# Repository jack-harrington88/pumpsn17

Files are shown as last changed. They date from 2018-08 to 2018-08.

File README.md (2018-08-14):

# Perpetual Sedimentation (PS) Prototype

**This page describes how to build a perpetual sedimentation prototype housing three syringe pumps. These pumps allow for a continuous delivery of particles.**

This project is a fork of the original DropletKitchen project; [Low-cost, High-performance Syringe Pumps for Microfluidics Applications](https://github.com/DropletKitchen/pumpsn17). Original source code of the project is provided under MIT License. The source may contain code under a different license, if this is the case it is stated in the LICENSE file. 

The designs and documentation in this repository is Copyright (c) 2018 Jack Harrington and made available under a [Creative Commons Attribution 4.0 International (CC BY 4.0)](https://creativecommons.org/licenses/by/4.0/) License.

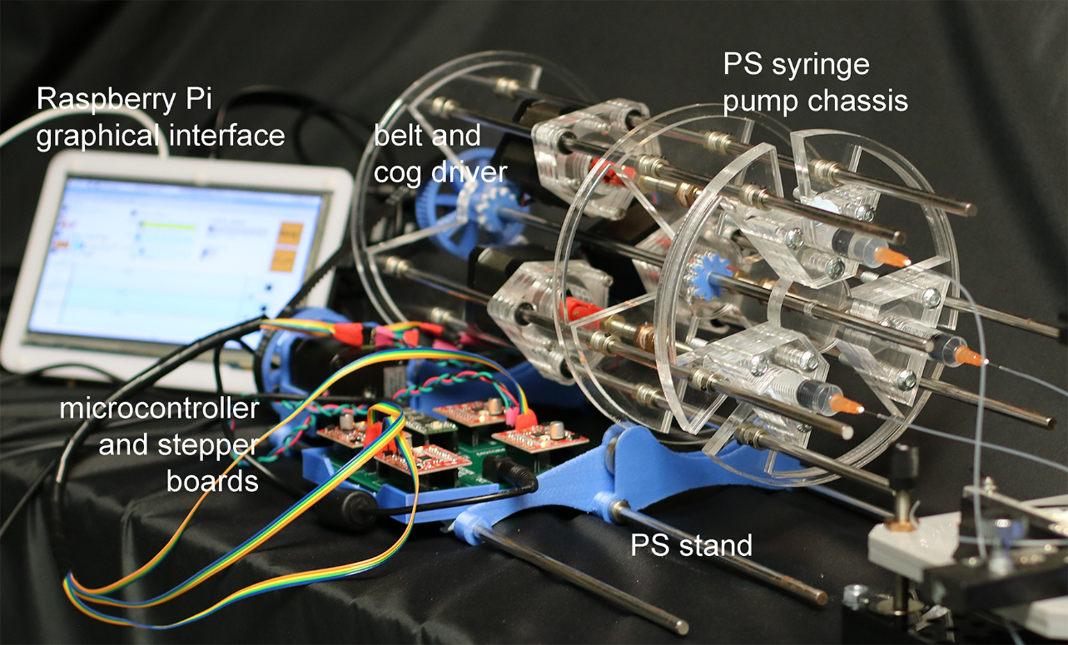
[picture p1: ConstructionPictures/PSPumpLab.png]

> The PS Pump prototype

## Introduction

The low-cost, high-performance syringe pumps from the droplet kitchen are suitable for a wide range of microfluidic applications, rivalling commercial pumps in quality at a fraction of the cost. The rapid sedimentation of particles often used in experiments (e.g. the DNA barcoded microbeads used in Drop-Seq) requires the use of expensive magnetic stirrers to actuate magnetic bars within the syringe. However, the DropSeq beads are fabricated using Toyopearl HW-65S resin, a brittle material that is prone to fracture during magnetic stirring. The perpetual sedimentation prototype provides a contactless solution to maintain particles in a suspended state to ensure continuous delivery.

The three PS syringe pumps work the same way as the original droplet kitchen pumps. The leadscrew is driven through a nut, pushing the plunger of the syringe at a controllable rate. A fourth motor controls the rotation of the chassis, rotating 360 degrees clockwise before turning 360 degree anticlockwise. This change of direction prevents the wires and tubing from continuously twisting. By loading well mixed syringes, the continuous rotation keeps particles evenly distributed throughout the syringe.

The prototype is relatively easy to construct for less than £500. Access to a laser cutter and 3d-printer is required - check a local makerspace/University or alternatively paid laser cutting and 3d-printing services are available online. Some experience with soldering/tinkering is advised.

The laser cut parts were designed in [CoralDRAW](https://www.coreldraw.com/en/) and each 3D print component was designed using [FreeCad](https://www.freecadweb.org/).
Modifications to the structure can be made by downloading and editing the [dxf file](https://github.com/jack-harrington88/pumpsn17/blob/master/PSPump_lasercut.dxf) and [FreeCad files](https://github.com/jack-harrington88/pumpsn17/tree/master/3d%20print/FCstd%20files).

## Bill of Materials
|	Item	|	Number	|	Purpose	|	Bought from	|	Part-no.	|	Approx. Cost (£)	|
|	-----------------------------------------------------------------------------------------	|	:---------:	|	:-------------:	|	--------------:	|	:----------:	|	:---:	|
|	Stepper Motor - NEMA17 - 400 steps (0.9 degree/step)	|	4	|	Stepper Motor	|	RS (can find cheaper)	|	535-0401	|	~108	|
|	Big Easy Stepper Driver	|	4	|	Stepper board	|	Hobbytronics	|	ROB-12859	|	~68	|
|	TEENSY3.2	|	1	|	Microcontroller	|	cpc-Farnell	|	SC13539	|	~17	|
|	Fine Hex Adjuster, 1/4"-80, 4" Long 	|	3	|	Leadscrew	|	Thorlabs	|	F25SS400	|	~30	|
|	Locking Phosphor-Bronze Bushing with Nut, 1/4”-80, L=0.50”	|	3	|	Leadscrew nut	|	Thorlabs	|	N80L6P	|	~21	|
|	Silver Steel 6 mm x 333 mm	|	10	|		|	Technobots	|	4426-006	|	~20	|
|	Zinc Collets 6 mm pk/4	|	48	|	Fasteners	|	Technobots	|	4609-060	|	~12	|
|	Linear Bearing LM6UU 6 mm Bushing	|	3	|	Slides motorpart	|	Technobots	|	4604-606	|	~3	|
|	Universal Coupling Body	|	3	|	Motor to screw connector	|	Technobots	|	4604-050	|	~9	|
|	Universal Coupling Insert - 5 mm	|	3	|	Motor to coupling	|	Technobots	|	4604-059	|	~6	|
|	Universal Coupling Insert - 1/4”	|	3	|	Coupling to screw	|	Technobots	|	4604-066	|	~9	|
|	306-3M-09 Timing Belt 3 mm Pitch, 9 mm Wide, 102 Teeth	|	1	|	Timing Belt	|	WychBearings	|	306-3M-09	|	~2	|
|	Shielded ball bearings (inner diameter 8 mm, outer 22 mm, 7 mm width)	|	4	|	Bearings	|	Simply Bearings or Amazon	|	608ZZ	|	~5 for 8	|
|	Stripboard	|	1	|	Mount for electronics	|	Technobots	|		|	~2	|
|	Sugru	|	1	|	Isolate PCB-headers	|	Amazon	|		|	~7	|
|	PCB headers and footers	|	some	|	Simple connectors	|	RS	|		|	~10	|
|	Various M3 Screws	|	Many	|		|	Hardware shop	|		|	~3	|
|	M6 Screws	|	Many	|		|	Hardware shop	|		|	~3	|
|	M6 Nuts	|	Many	|		|	Hardware shop	|		|	~3	|
|	12V/>=5A power supply	|	1	|		|	CPC-Farnell	|		|	~20	|
|	Ribbon cable (15ft)	|	4 m	|		|	Technobots	|		|	~4	|
|	micro USB cable	|	1	|		|	CPC-Farnell	|		|	~3	|
|	Acrylic (410 x 280 x 5 mm)	|	Pack of 5	|		|	TechSoft	|		|	~22	|
|	PLA Filament (1.7 mm)	|	>31 m	|		|	Farnell	|		|	~26	|
|		|		|		|		|	Total	|	413	|

## Assembly

* Laser cut each of the parts found in the [.dxf file](https://github.com/jack-harrington88/pumpsn17/blob/master/PSPump_lasercut.dxf)
* 3d-print the required number of pieces at 15% infill.

### Laser Cut and 3D Printed Components

|Name|Method|Number|file location|
|----|:----------:|:-------------|-------------:|
|A|Laser Cut|2|[dxf file](https://github.com/jack-harrington88/pumpsn17/blob/master/PSPump_lasercut.dxf)|
|B|Laser Cut|1|[dxf file](https://github.com/jack-harrington88/pumpsn17/blob/master/PSPump_lasercut.dxf)|
|C|Laser Cut|1|[dxf file](https://github.com/jack-harrington88/pumpsn17/blob/master/PSPump_lasercut.dxf)|
|D|Laser Cut|1|[dxf file](https://github.com/jack-harrington88/pumpsn17/blob/master/PSPump_lasercut.dxf)|
|E|Laser Cut|1|[dxf file](https://github.com/jack-harrington88/pumpsn17/blob/master/PSPump_lasercut.dxf)|
|F|Laser Cut|12*|[dxf file](https://github.com/jack-harrington88/pumpsn17/blob/master/PSPump_lasercut.dxf)|
|G|Laser Cut|12|[dxf file](https://github.com/jack-harrington88/pumpsn17/blob/master/PSPump_lasercut.dxf)|
|ArmBearingStand|3d Print (4.10m)|1|[ArmBearingStand.stl](https://github.com/jack-harrington88/pumpsn17/blob/master/3d%20print/ArmBearingStand.stl)|
|BearingStand|3d Print (2.76m)|2|[BearingStand.stl](https://github.com/jack-harrington88/pumpsn17/blob/master/3d%20print/BearingStand.stl)|
|MotorStand|3d Print (8.83m)|1|[MotorStand.stl](https://github.com/jack-harrington88/pumpsn17/blob/master/3d%20print/MotorStand.stl)|
|StandPulley|3d Print (4.97m)|1| [StandPulley.stl](https://github.com/jack-harrington88/pumpsn17/blob/master/3d%20print/StandPulley.stl) |
|PumpPulley|3d Print (4.97m)|1| [PumpPulley.stl](https://github.com/jack-harrington88/pumpsn17/blob/master/3d%20print/PumpPulley.stl) |
|Cog|3d Print (0.99m)|2| [cog.stl](https://github.com/jack-harrington88/pumpsn17/blob/master/3d%20print/cog.stl)|

\* *or more depending on size of syringe*

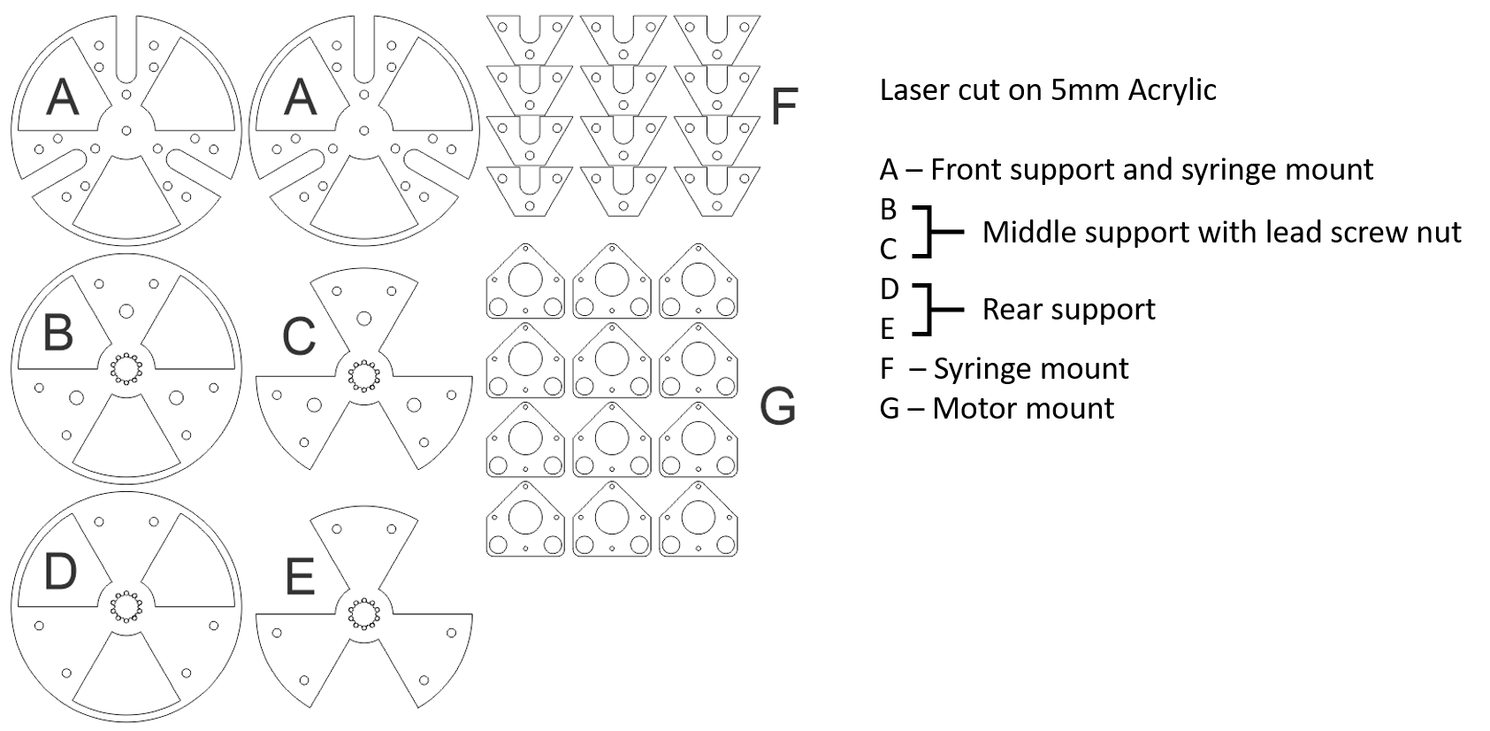
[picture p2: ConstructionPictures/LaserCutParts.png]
 
> The laser cut parts for the syringe pump chassis.

### Assembly

As with the assembly of the droplet kitchen syringe pumps:
* For 3 of the motors; attach the universal coupling inserts and bodies to each of the motor shafts.
* Screw four part Gs onto the three stepper motors. 
* Insert each lead screw.

Additionally:
* Add an M3 nut into the rectangular hole in each of the cogs and pulleys and insert an M3 screw down through the top. See figure below.

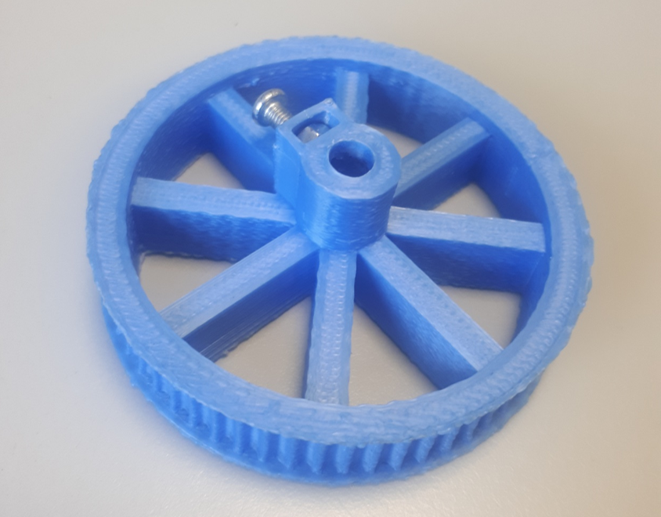
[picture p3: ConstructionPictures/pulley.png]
 
> The pulley with a grub screw and nut.

#### The Syringe Pump Chassis

Required; all remaining laser cut components, 2x cogs, 1x pump pulley, the 3 motor parts, 3x lead screw nut, 7x steel rods, 36x collets. 

Following the figure below:

  1. Align parts D and E together, pushing 2 rods through each segment and fastening together with collets.

  2. Slide the three stepper motor mounts on to each pump segment.

  3. Fasten parts B and C together using the lead screw nut.

     Slide the joined B & C components onto the rods (approx. 190 mm from parts D & E) securing in place with collets.
   
     Thread the lead screw through the lead screw nuts.
   
  4. Slide two part A pieces onto the rods and fasten with collets approx. 80 mm from B & C.

  5. Using M6 Nuts and screws, fasten four part Fs onto the two part As (more can be used for larger syringes).

  6. Push a steel rod through the two printed cogs.

     Align the cogs with the cog-shaped holes in D&E and B&C parts and screw the grub screws tight.
   
     At the rear end of this central rod, attach the pump pulley and tighten the grub screw.

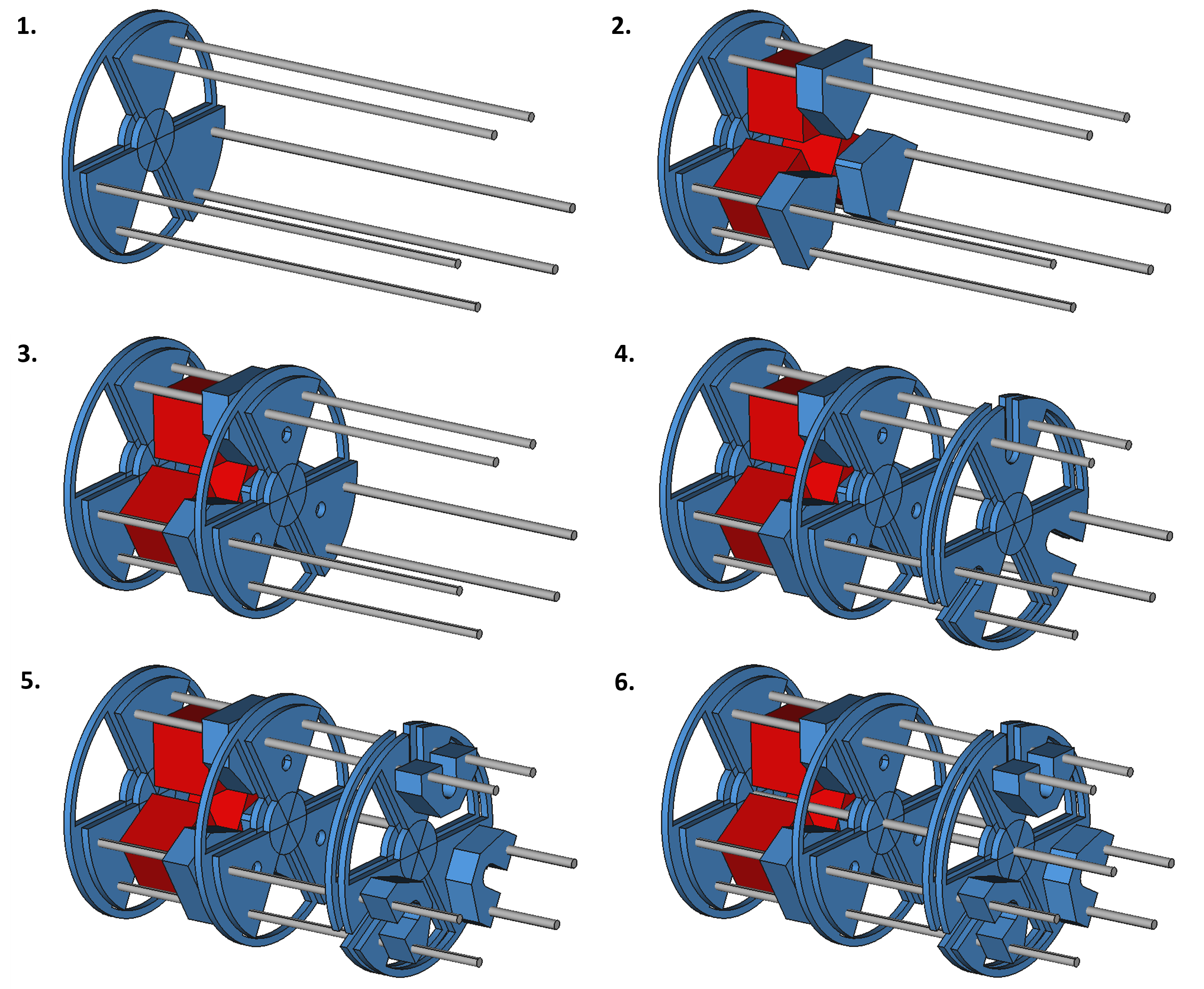
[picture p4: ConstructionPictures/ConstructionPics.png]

> The construction of the syringe pump chassis.

#### The PS Stand
Required; 3x steel rods, 1x arm bearing stand, 1x motor stand, 2x bearing stand, 4x ball bearings, 12x collets.

* Firmly push each ball bearing onto the two bearing stands.
* Attach one bearing stand to the motor stand and the other to the arm bearing stand.
* Thread three rods through the holes in either stand piece.
* Screw the remaining stepper motor onto the motor stand using M3 screws (see below, left).
* Adjust the distance and orientation to allow the three pumps in the overall chassis to rest evenly on top of the ball bearings, fastening in place with collets.

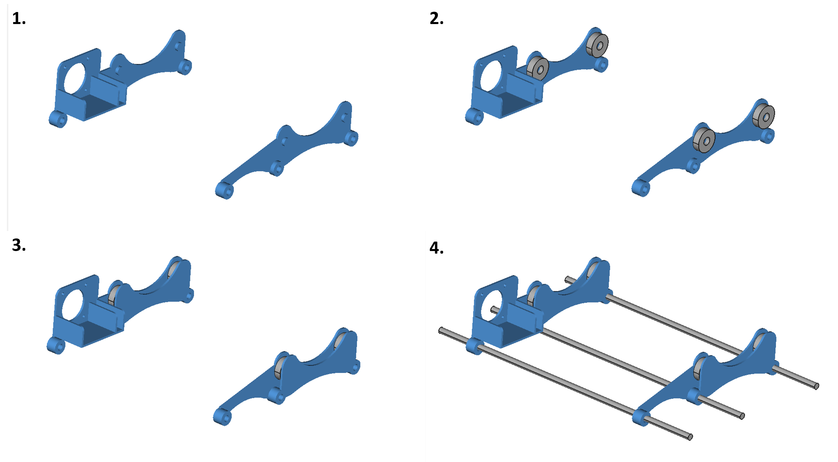
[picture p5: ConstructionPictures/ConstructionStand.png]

> Construction of the PS stand.

* Push the stand pulley onto the stepper motor, tightening the grub screw.
* Attach the belt to both pulleys. There should be a tight fit without the pumps lifting from the ball bearings (see above, right. 

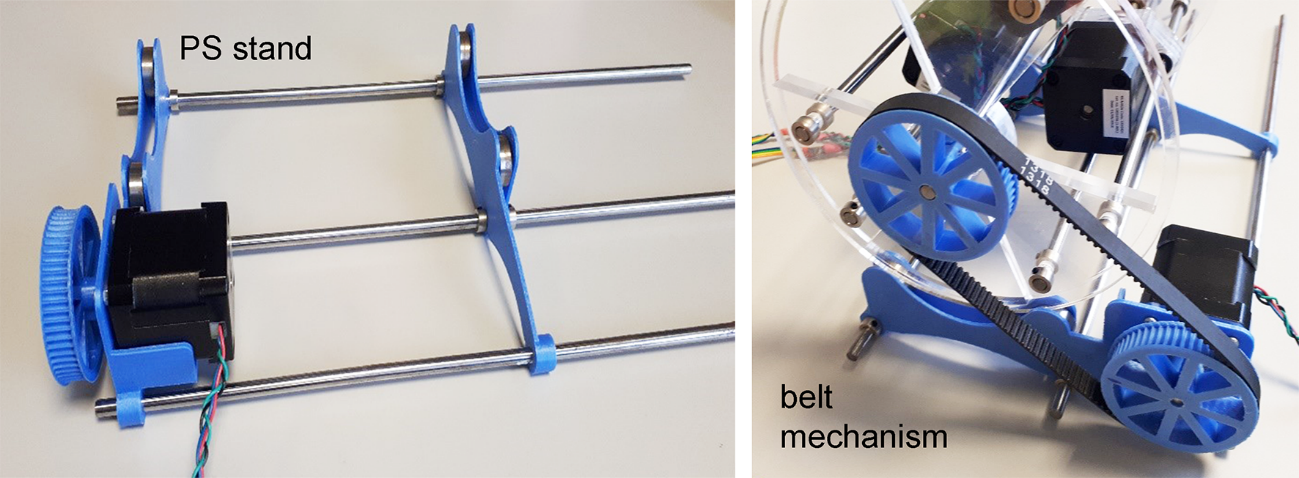
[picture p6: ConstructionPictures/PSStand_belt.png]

> The PS stand and belt mechanism.

### Electronics

* The electronics are set up the same as the [droplet kitchen pumps](https://github.com/DropletKitchen/pumpsn17/blob/master/README.org#electronics).
* For the first three stepper motors - extend the length of wiring using the ribbon wire and PCB-connectors. The length of wire between motor and motor driver should be >0.9 m. This comfortably allows enough room for the complete rotation of the PS pumps. 
* The fourth stepper motor (pins 11  & 12 - direction and speed respectively) controls the rotation.

# Software for the Pertpetual Sedimentation Pumps

The pumps are controlled in the same way as the [droplet kitchen pumps](https://github.com/DropletKitchen/pumpsn17).
* Download all the files from [PSPumpSoftware](https://github.com/jack-harrington88/pumpsn17/tree/master/PSPumpSoftware).
* Upload the Flexible3or4Pumps.ino to the Teensy microcontroller through the [Arduino IDE](https://www.pjrc.com/teensy/td_download.html) .
* [Pure Data](https://puredata.info/) is used for the frontend and calculating flow rates and rotation speeds.
* Place the PSPump.pd, PSPumpGOP.pd and o.io.slipserial.pd into a folder together and run through Pure Data (when controlling the pumps opening the PSPump.pd and PSPumpGOP.pd together helps prevent the stepper motor from 'missing' a turn).

# Syringe Pump and Rotation Control

The syringe pumps are controlled exactly as in the droplet kitchen pumps, moving the slider to the desired rate. Syringe diameters can also be altered with the corresponding buttons.
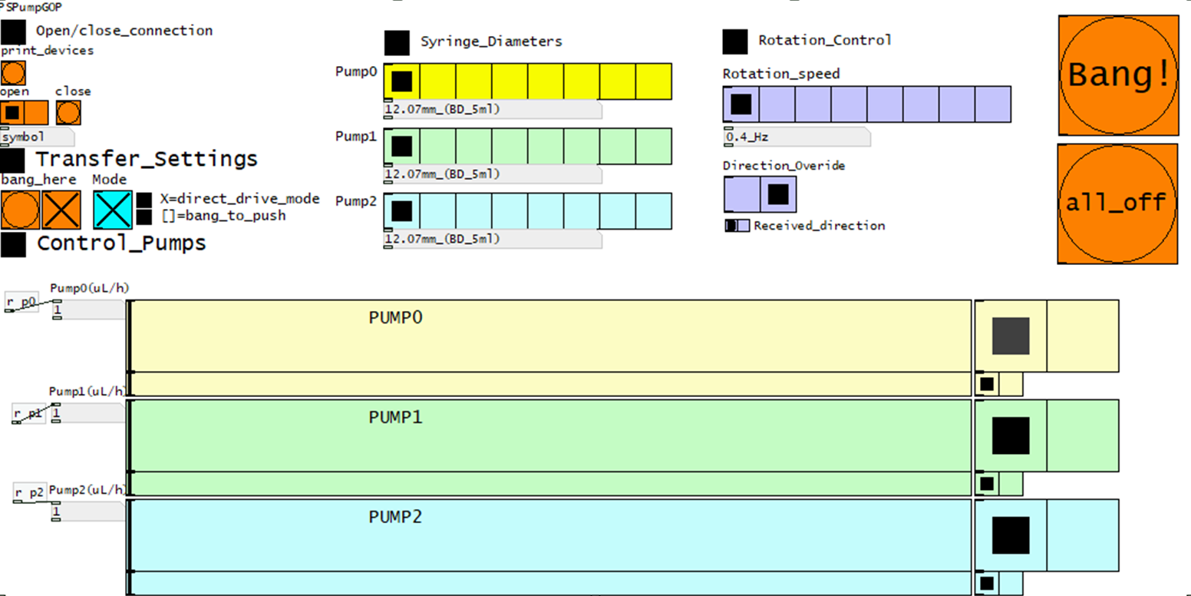
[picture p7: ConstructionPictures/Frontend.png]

> The Pure Data front end to control syringe pumps and chassis rotation.

The rotation rate is controlled through the blue radio buttons labelled "Rotation_speed" (far left stopping rotation). Below these controls is a manual override on the direction and the feedback direction from the microcontroller. Pressing the all_off button stops all 3 pumps and halts rotation. The Bang! button sets the syringe pumps to flow at a specific rate which can be configured in PSPumpGOP.pd. Changes to the speeds and degree of rotation is also easily done by modifying the PSPumpGOP.pd as below. 

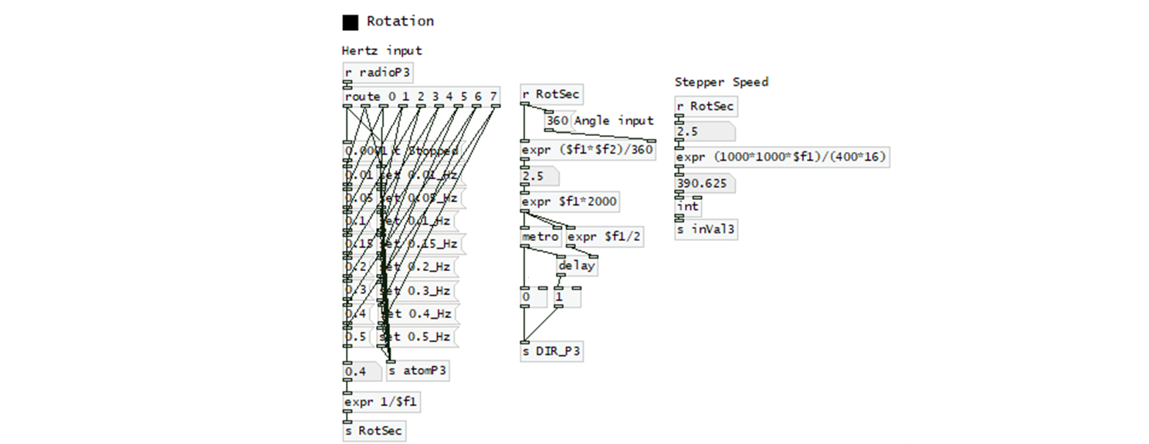
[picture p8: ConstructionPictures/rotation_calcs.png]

> The chassis rotation calculations.

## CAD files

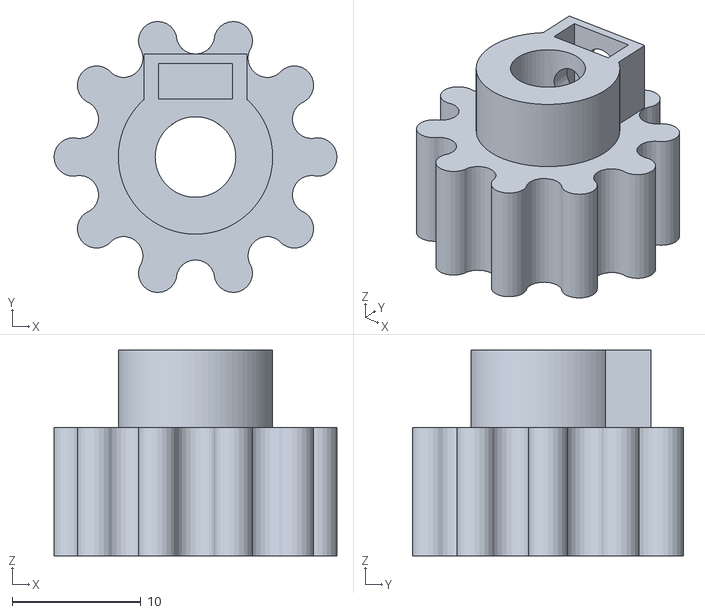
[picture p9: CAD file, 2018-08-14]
3d print/cog.stl
22.0 x 21.1 x 16.0

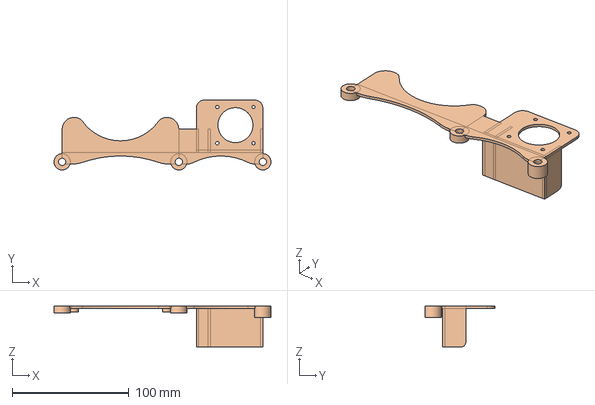
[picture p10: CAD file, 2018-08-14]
3d print/FCstd files/MotorStand.FCStd
186.0 x 60.0 x 35.0 mm

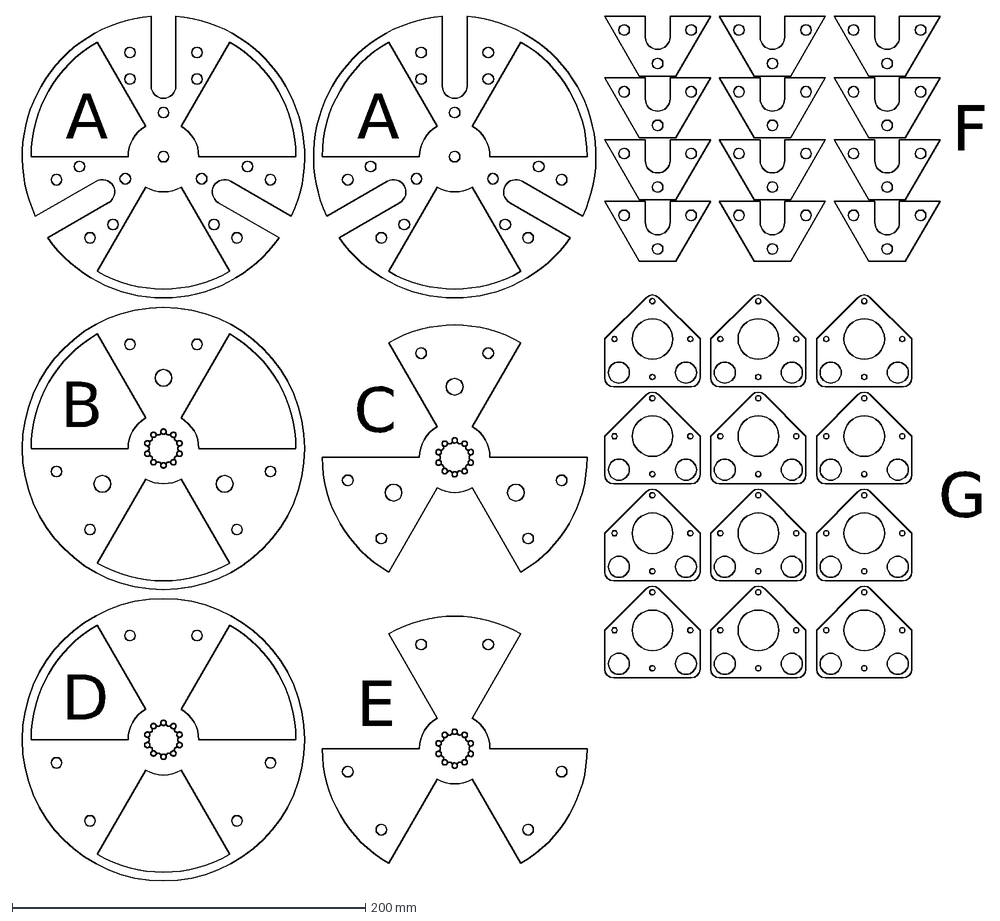
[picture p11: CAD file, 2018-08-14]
PSPump_lasercut.dxf
A
B
D
C
E
F
G

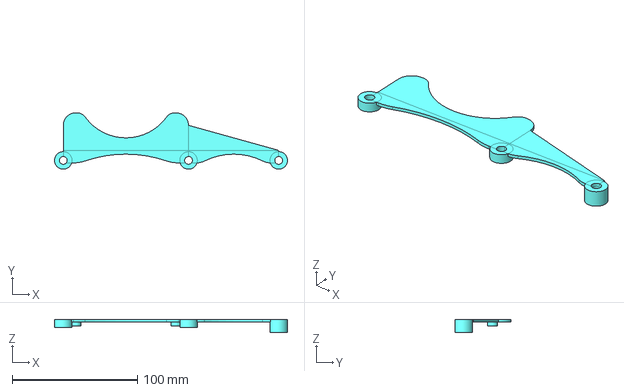
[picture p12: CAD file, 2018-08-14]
3d print/FCstd files/ArmBearingStand.FCStd
186.0 x 45.0 x 10.0 mm

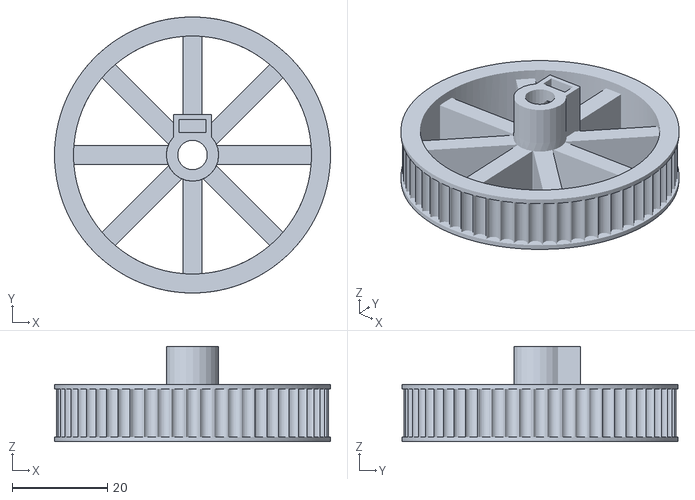
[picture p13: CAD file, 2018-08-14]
3d print/PumpPully.stl
58.0 x 58.0 x 20.0

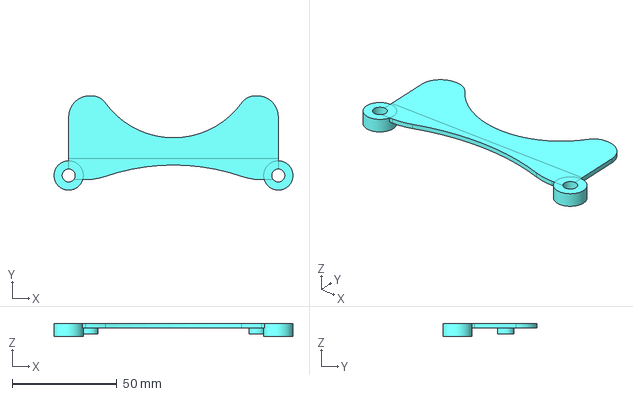
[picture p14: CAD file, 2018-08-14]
3d print/FCstd files/BearingStand.FCStd
114.0 x 45.0 x 6.00 mm

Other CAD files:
3d print/StandPully.stl
3d print/ArmBearingStand.stl
3d print/BearingStand.stl
3d print/MotorStand.stl
